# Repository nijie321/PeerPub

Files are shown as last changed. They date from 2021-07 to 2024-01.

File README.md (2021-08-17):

# PeerPub 
 Tracking two rats independently during oral operant self-administration of solutions (e.g. sucrose, alcohol, opioids).

## Program Structure

   Main Program: main.py (main_test.py) is the entry program. This program handles session command and rat ID
   scanning, adjusting the pump position, and finally calling the operant.py as a subprocess.
   Note that this program does not exit after calling the subprocess. It it kept alive, as the
   main thread, to record rat's ID when they poke their head near the antenna. Rat's ID are
   stored in _active and _inactive files located in the /home/pi/ directory.
   
   Operant Program: operant.py (operant_test.py) is the program which main invoke at the end of it's executation.
   This program handles saving each data point to corresponding data files.

   Pump Driver Program: pump_move.py is the program that is used, as a higher level abstraction, to drive the stepper motor using underlying gpiozero/RPi.GPIO library. This program mainly consist of the PumpMove class which contains a move() class for "rotating" the motor (forward and backward). The __del__ method need to be call at the end of each use to 'shutoff' the motor. This prevent the motor driver from overheating (there are more efficient ways to do this).
   
   Activity Counter Program: Rat's activity (inactive lick, active lick, and etc) are being represent as an instance of RatActivityCounter.

   PumpCalibration Program: Currently, the motor step size is not accurate enough. The pump's step need to be modified from time to time. This program prompt the user to measure the amount of solution the pump push out and enter that amount. Then the program will automatically re-adjust the step size.

## Configuration
   - Files

     - /home/pi/peerpub_config.json
        This file stores 3 information: device ID, session number/ID, and stepper motor step size. (The session number is increament by 1 each time the program start)

     - /home/pi/openbehavior/PeerPub/python/session_configuration.csv
        This file is used by the program to read in the session information. 

     - /home/pi/openbehavior/PeerPub/python/config.py
        This file stores different directory paths. Note that these path are all absolute paths. There's a "get_sessioninfo" function which takes in a argument "sessionid" to retrive session information from "session_configuration.csv" mentioned above. A good practice is to put related configuration functions in this file and import then when needed.

## Utility Scripts

   **check_empty_program.sh**: a script that check the size of every python file in the python/ directory. If one or more files are empty the script then reclone the entire repository.

   **check_network.sh**: a script that check the network connection right after the device boots up and ask user for action when the device was not able to connect to network.

## Program Overview
The main (main_test.py) program is used to read/scan the pre-configured command RFID stored in 'session_configuration.csv' file under python directory. After the command ID is scaned, the program proceed to ask for scanning rat's ID. The time between scanning rat's ID and command ID is the time for adjusting the pump position (e.g. after the rat's ID are scanned, the pump adjustment are disabled to avoid driver board overheating). After the rat's ID are scanned, the main program spawns a new operant (operant_test.py) program by passing in the necessary arguments and run it in the background. Note that because the operant program is a thread, the main program is kept alive (e.g. running in parallel with the operant program). The main program is tasked with reading the rat's ID when they poke their head into the active or inactve spout (disctinguished by the length of characters: 10 for inactive poke and 8 for active poke).

## Parts and GPIO Pin Connections Table

   [DRV8834 Low-Voltage Stepper Motor Driver](https://www.pololu.com/product/2134), [Stepper Motor](https://www.pololu.com/product/2267), [Belker Universal AC Adapter 3-12V](https://www.amazon.com/Belker-Adjustable-Universal-Household-Electronics/dp/B07NKZCWT1/ref=asc_df_B07NKZCWT1/?tag=hyprod-20&linkCode=df0&hvadid=366402536789&hvpos=&hvnetw=g&hvrand=9548953669677245441&hvpone=&hvptwo=&hvqmt=&hvdev=c&hvdvcmdl=&hvlocint=&hvlocphy=9013532&hvtargid=pla-800552094134&psc=1&tag=&ref=&adgrpid=75347436439&hvpone=&hvptwo=&hvadid=366402536789&hvpos=&hvnetw=g&hvrand=9548953669677245441&hvqmt=&hvdev=c&hvdvcmdl=&hvlocint=&hvlocphy=9013532&hvtargid=pla-800552094134)
   | Pins on the driver | GPIO pin slot on the Pi, external power supply, and the stepper motor|
   |--------------------|------------------------|
   |      VMOT         |      **AC Adapter** - positive end of LED Terminal Adapter    |
   |     GND |   **AC Adapter** - negative end of LED Terminal Adapter |
   | B2, B1, A1, A2 |    **Stepper Motor** - Black, Green, Red, and Blue wire respectively      |
   |      GND |    **Pi** - Any GND pin                |
   |      M0, M1 | **Pi** - GPIO 17 and 22       |
   |     SLP | **Pi** - Any 3v3 pin          |
   |      STEP | **Pi** - GPIO 6            |
   |      DIR | **Pi** - GPIO 26 |
   
   [Adafruit 12-Key Capacitive Touch Sensor - MPR121](https://www.adafruit.com/product/1982)
   | Pins on the driver | GPIO pin slot on the Pi and external wires|
   |--------------------|------------------------|
   |  SCL, SDA | **Pi** - GPIO 3 and 2 respectively |
   |  3Vo | **Pi** - Any 3v3 pin|
   |  GND | **Pi** - Any GND pin|
   |  0 | **external wire** - inactive wire|
   |  1 | **external wire** - active wire|

   [Limit Switch](https://www.amazon.com/MXRS-Hinge-Momentary-Button-Switch/dp/B07MW2RPJY/ref=lp_5739467011_1_7)
   | Pins on the driver | GPIO pin slot on the Pi and external wires|
   |--------------------|------------------------|
   |  Normally Open (NO) | **Pi** - any 5V pin|
   |  Forward Limit - Contact Point (C) | **Pi** - GPIO 24|
   |  Backward Limit - Contact Point (C) | **Pi** - GPIO 23|

   [Push Button](https://www.amazon.com/DAOKI-Miniature-Momentary-Tactile-Quality/dp/B01CGMP9GY/ref=asc_df_B01CGMP9GY/?tag=hyprod-20&linkCode=df0&hvadid=309774137275&hvpos=&hvnetw=g&hvrand=7843520885449353644&hvpone=&hvptwo=&hvqmt=&hvdev=c&hvdvcmdl=&hvlocint=&hvlocphy=9013532&hvtargid=pla-640514760452&psc=1)
   | Pins on the driver | GPIO pin slot on the Pi|
   |--------------------|------------------------|
   | Forward Button | **Pi** - GPIO 5|
   | Backward Button | **Pi** - GPIO 27|
   **Connect resistor and GND correspondingly**
   
   [Pixel Ring](https://www.adafruit.com/product/1643)
   | Pins on the driver | GPIO pin slot on the Pi|
   |--------------------|------------------------|
   | IN | **Pi** - GPIO 18|
   | GND | **Pi** - any GND pin |
   | 5V DC | **Pi** - any 5V pin |

## Resources
   [Raspberry Pi Stepper Motor Tutorial](https://www.rototron.info/raspberry-pi-stepper-motor-tutorial/)  
   [Raspberry Pi Stepper Motor Control with nema17](https://makersportal.com/blog/raspberry-pi-stepper-motor-control-with-nema-17)  
   [OpenSourceSyringePump](http://cavarnon.com/syringepump)  
   [How to Control a stepper motor with DRV8825 driver and Arduino](https://www.makerguides.com/drv8825-stepper-motor-driver-arduino-tutorial/)

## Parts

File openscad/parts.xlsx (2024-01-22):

Item | Part | Quantity | Supplier | Link
Pump Parts | Pump power | 1 | Amazon | https://www.amazon.com/Belker-Adjustable-Universal-Household-Electronics/dp/B07NKZCWT1
 | NEMA 17 Stepper Motor | 1 | Pololu | https://www.pololu.com/product/2267
 | 12" Actobotics Channel | 1 | ServoCity | https://www.servocity.com/12-0-channel
 | Actobotics Side Tapped Pattern Mount B | 1 | ServoCity | https://www.servocity.com/90-quad-hub-mount-b
 | Actobotics NEMA 17 Stepper Mount | 1 | ServoCity | https://www.servocity.com/nema-17-stepper-motor-mount
 | Pump rod | 1 | Amazon | https://www.amazon.com/uxcell-Stainless-Copper-Thread-Printer/dp/B07R1H5ZMV?s=industrial
 | Rod bearing | 1 | Amazon | https://www.amazon.com/Bearings-Double-Shielded-Miniature-Skateboard/dp/B07H83VV6B
 | Rod coupling | 1 | Amazon | https://www.amazon.com/AFUNTA-Flexible-Couplings-Compatible-Machines/dp/B07JL1QYLS
 | 4 pin connector | 1 | Amazon | https://www.amazon.com/mxuteuk-Female-Connector-Adapter-Electrical/dp/B083GR7FQF
 | 3 pin connector | 1 | Amazon | https://www.amazon.com/BTF-LIGHTING-Connectors-WS2812B-WS2811-WS2812/dp/B01DC0KIT2
 | Limit Switch with Lever 2 Pack | 1 | ServoCity | https://www.servocity.com/spdt-miniature-lever-snap-action-micro-switch-2-pack
Box Parts | Raspberry Pi 3B | 1 | Rasperrypi | https://www.raspberrypi.com/
 | Pi screen | 1 | Dfrobot | https://www.dfrobot.com/product-1784.html
 | Pololu DRV8825 Stepper Motor Driver | 1 | Pololu | https://www.pololu.com/product/2133
 | Touch sensor board | 1 | Adafruit | https://www.adafruit.com/product/1982
 | Button | 1 | Amazon | https://www.amazon.com/Gikfun-12x12x7-3-Tactile-Momentary-Arduino/dp/B01E38OS7K
 | Button board | 1 | Amazon | https://www.amazon.com/LAMPVPATH-Prototype-Breadboard-Universal-Printed/dp/B07JDZDPVQ
 | Led ring | 1 | Adafruit | https://www.adafruit.com/product/2852
 | Rfid scanner | 1 | Amazon | https://www.amazon.com/YARONGTECH-125khz-reader-EM4100-desktop/dp/B078TK8KYL/?th=1
 | connector cables | 1 | Amazon | https://www.amazon.com/Antrader-Breadboard-Dupont-Arduino-Raspberry/dp/B07RXK9SLW?th=1
 | Resistor(200ohm, 1/2w) | 1 | Amazon | https://www.amazon.com/EDGELEC-Resistor-Tolerance-Multiple-Resistance/dp/B07QDXV1KF
Other Parts | 30 cc Syringe 10 pack | 1 | Amazon | https://www.amazon.com/Easy-Glide-30CC-Syringe-Sterile/dp/B08HV25ZN2
 | screw and nuts (#6-32)

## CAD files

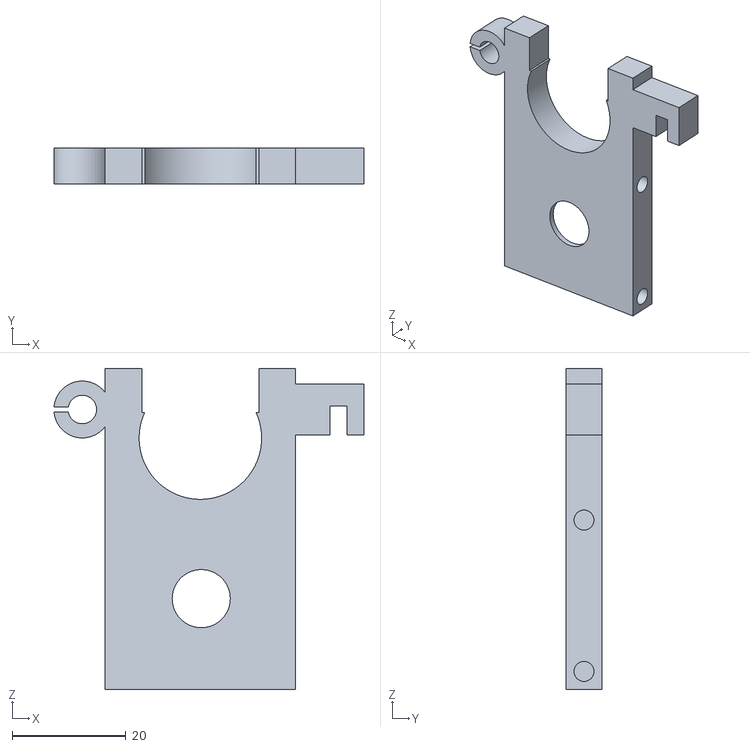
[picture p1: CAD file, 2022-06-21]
openscad/pump_top.stl
54.4 x 6.30 x 56.4

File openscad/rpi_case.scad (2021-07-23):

//include <driverPlate.scad>;
$fn=50;


// define global variables (measurments, unit = mm)
lcdWidth = 121.4 + 25 - 25 ;
lcdWidthForScrewHolder = 121.4 ;
lcdThickness = 7.91;
lcdHeight = 76.80 ;
baseBoardThickness = 2;//.5;


squareHeight=7.5;
squareWidth=7.5;
squareThickness= 1;//2.5;

screwInnerRadius = 1.5;//2.56;
smallChipWidth = 19.18;
smallChipHeight = 33.32;

heightToScrew = 13.15; //12.88

smallChipThickness = 1.69;
smallChipHoleRadius = 2.42;
screenWidth = 109.8;
screenHeight = 66.4 ;

leftSideInputPortsWidth = 50.67;
leftSideInputPortsHeightFromBase = 21.36;
leftSideInputPortsHeight = 8.05;

endInputPortsHeightFromBase = 30.96;
endInputPortsWidth = 52.37;




overallWidth=77.33 ;
    width=72.91 ;
    protrodingWidth=overallWidth - width;
    protrodingThickness=2.2;
    
    
module base(){
rotate([0,90,0]) color("red") cube([baseBoardThickness+1, lcdWidth, lcdHeight], center=true);
}

module makeRearendWall(head=1){

    overallWidth=78.4;
    width=72.91 -2.5;
    protrodingWidth=overallWidth - width;
    protrodingThickness=2.2;
    
    
//    height=77.33;
//    
//    overallWidth=77.33;
//    width=77.48;//72.91;
//    protrodingWidth=overallWidth - width;
//    protrodingThickness=2.2;
    // front wall
    if(head ==  1){
        translate([0,(lcdWidthForScrewHolder/2 - (squareHeight/2)) + (squareHeight/2+(baseBoardThickness+1) /2) ,(width/2) - ((baseBoardThickness+1) /2)]) cube([lcdHeight+((baseBoardThickness+1)*2),baseBoardThickness+1,width],center=true);    
    }
    echo((lcdWidthForScrewHolder/2 - (squareHeight/2)) , lcdWidth, lcdWidth - ((lcdWidthForScrewHolder/2 - (squareHeight/2))))
    
    // end wall
    if(head == 0){
//    ((width/2)-((protrodingThickness)/2))    
                translate([0,-(((protrodingThickness) /2)+(lcdWidth/2)),width/2-(baseBoardThickness-1)]) cube([lcdHeight+((baseBoardThickness+1)*2),protrodingThickness,width ],center=true);
    }
    
}



module slider(){
    width = 77.37;
    height = 41.26;
    thickness = 2.11;        
    
    color("red") translate([0,0,lcdHeight/2 + (thickness/2) + (baseBoardThickness/2)]) cube([height, width,thickness],center=true);    
}


module makeTopBottomCover(top=true){
    overallWidth=78.4 ;
    width=72.91 ;
    protrodingWidth=overallWidth - width;
    protrodingThickness=2.2;
   if(top){
       // lcdHeight/2
       
//        (lcdWidth) +(baseBoardThickness+1)*2
   translate([0,0,width - (baseBoardThickness) -1]) cube([lcdHeight+((baseBoardThickness+1) *2), lcdWidth , baseBoardThickness+1],center=true);    
   }
   
   if(!top){
       //+ ((baseBoardThickness+1) *2)
       cube([lcdHeight+((baseBoardThickness+1) *2), (lcdWidth) ,baseBoardThickness+1],center=true);
   }
   
}

cutoff1 = (lcdHeight/2) + (baseBoardThickness/2);
xTempVar = ( (lcdHeight/2) + (baseBoardThickness/2) ) + ( ( (lcdHeight+((baseBoardThickness+1)*2)) )/2 - (cutoff1+ (baseBoardThickness/2) ) ) /2;
yTempVar = -( (lcdWidth/2) + ((baseBoardThickness/2)) + ( ((baseBoardThickness+1)/2) - (baseBoardThickness/2) ) );
zTempVar = 40;

module fourVerticalPoles(topPoles=true, head=true){
    radius = 1.50;//baseBoardThickness/2;
if(topPoles){

if(head){
color("red") translate([xTempVar, yTempVar, zTempVar]) cylinder(r=radius,h=20,center=true);
color("red") translate([-xTempVar, yTempVar, zTempVar]) cylinder(r=radius,h=20,center=true);
}
else{
color("red") translate([xTempVar, -yTempVar, zTempVar]) cylinder(r=radius,h=20,center=true);
color("red") translate([-xTempVar, -yTempVar, zTempVar]) cylinder(r=radius,h=20,center=true);
}

}

if(!topPoles){
color("red") translate([xTempVar,yTempVar,0]) cylinder(r=baseBoardThickness/3,h=20,center=true);
color("red") translate([-xTempVar,yTempVar,0]) cylinder(r=baseBoardThickness/3,h=20,center=true);
}

}

//color("blue") cube([lcdHeight+((baseBoardThickness+1) *2), (lcdWidth + ((baseBoardThickness+1) *2)) ,baseBoardThickness+1],center=true);


depth = squareThickness + 10;
module placeScrewHolder(x=(lcdHeight/2 - (squareWidth/2)) , y=(lcdWidthForScrewHolder/2 - (squareHeight/2)) , z=squareThickness * 1.5 + 15.6, rearEnd=false, flag=1) {
    
    if(rearEnd==false){
    
    translate([x,y,z])
    difference(){
            cube([squareWidth,squareHeight,squareThickness],center=true);
            color("blue") cylinder(r=screwInnerRadius,h=squareThickness,center=true);
    }
    
    }
    
    if(rearEnd==true){
        if(flag == 1){
            translate([x,y,z])
            difference(){
                    cube([squareWidth+1,squareHeight+1,squareThickness],center=true);
                    color("blue") translate([1,-1,0]) cylinder(r=screwInnerRadius+.1,h=squareThickness,center=true);    
            }
        }
            
        if(flag == 2){
            translate([x,y,z])
            difference(){
                    cube([squareWidth+1,squareHeight+1,squareThickness],center=true);
                    color("blue") translate([-1,-1,0]) cylinder(r=screwInnerRadius+.1,h=squareThickness,center=true);            
        }
    }
    }
}

module placeCornerScrewHolder(x=0,y=0,z=0){
    translate([x,y,z])
    difference(){
    color("red") cube([squareWidth,squareHeight,depth],center=true);
    translate([0,0,(depth/2)/2]) color("blue") cylinder(r=screwInnerRadius,h=depth/2,center=true);
    }
}

//placeScrewHolder(x=(lcdHeight/2 - (squareWidth/2)),y=(lcdWidth/2 - (squareHeight/2)),z=((baseBoardThickness+1)/2) + (squareThickness/2) + heightToScrew);


toTranslateX = (lcdHeight/2) - (squareWidth/2);
toTranslateY = (lcdWidth/2) - (squareHeight/2);
//toTranslateZ = (lcdHeight/2) - ((baseBoardThickness+1)/2) - (depth/2);
//toTranslateZ =  depth/2 + ((baseBoardThickness+1)/2) + depth + width/2 + baseBoardThickness+1;
toTranslateZ = 1.5*depth + 1.5*(baseBoardThickness+1) + width/2 + 5.4;//2.5;

toTranslateYBottom = ( (lcdWidth/2) - (depth/2));
toTranslateZBottom =   (squareHeight/2) + ( (baseBoardThickness+1) / 2) + 15;
module makeScrewHolders(){
    
translate([0,0,-1.3]) union(){
    placeScrewHolder(rearEnd=true,flag=2);

    placeScrewHolder(x=-(lcdHeight/2 - (squareWidth/2)), rearEnd=true);
        

    placeScrewHolder(y= -(lcdWidthForScrewHolder/2 - (squareHeight/2) ) );

    placeScrewHolder(x=-(lcdHeight/2 - (squareWidth/2)),y=-(lcdWidthForScrewHolder/2 - (squareHeight/2)));
}
//placeScrewHolder(y=-(lcdWidth/2 - (squareHeight/2)));



// top four screw holder
//placeCornerScrewHolder(x=toTranslateX,y=-toTranslateY,z=toTranslateZ - 2.5);
placeCornerScrewHolder(x=toTranslateX,y=(lcdWidthForScrewHolder/2 - (squareHeight/2)),z=toTranslateZ - 2.5);
    
placeCornerScrewHolder(x=-toTranslateX,y=-toTranslateY + 11,z=toTranslateZ - 2.5);        
//placeCornerScrewHolder(x=-toTranslateX,y=(lcdWidthForScrewHolder/2 - (squareHeight/2)),z=toTranslateZ - 2.5); 

 

translate([toTranslateX,-toTranslateYBottom, toTranslateZBottom + heightToScrew]) rotate([90,0,0]) placeCornerScrewHolder();
translate([-toTranslateX,-toTranslateYBottom,toTranslateZBottom + heightToScrew]) rotate([90,0,0]) placeCornerScrewHolder();


color("green") translate([toTranslateX,-toTranslateYBottom, toTranslateZBottom + heightToScrew + 28.70]) rotate([90,0,0]) placeCornerScrewHolder();
color("green") translate([-toTranslateX,-toTranslateYBottom,toTranslateZBottom + heightToScrew + 28.70]) rotate([90,0,0]) placeCornerScrewHolder();       
}

extraBoardWidth = (smallChipHeight * 2) + 10;
extraBoardHeight = smallChipWidth + 5;

module extraBaseExtensions(){
// add extra base to hold two additional modules

//color("blue") translate([lcdHeight/2 + (smallChipWidth/2) + 5 ,0,0]) 
    cube([extraBoardHeight, ( (baseBoardThickness+1) *2) + (lcdHeight),(baseBoardThickness+1)], center=true);
}

GPIOSlotsWidth = 50.76/2;
GPIOSlotsHeight = 12.5;


module makeChipSlot(firstSlot=true){
    if(firstSlot){
translate([0,(smallChipHeight/2 + ((baseBoardThickness+1)/2) ),((baseBoardThickness+1) /2)- (smallChipThickness/2)]) cube([smallChipWidth,smallChipHeight,smallChipThickness],center=true);    
        }
        
     if(!firstSlot){
         translate([0,-(smallChipHeight/2 +((baseBoardThickness+1)/2)) ,((baseBoardThickness+1) /2) - (smallChipThickness/2)]) cube([smallChipWidth,smallChipHeight,smallChipThickness],center=true);
     }

}



h1 = (baseBoardThickness+1) - (smallChipThickness);

// extended base with two slots for the two additional sensors.
module sensorSpace(){
    
difference(){
    
difference(){
// extended base (to end)
extraBaseExtensions();
    // making slots for two sensors
    makeChipSlot(firstSlot=true);
    makeChipSlot(firstSlot=false);
}

// make four holes for the purpose of mounting two sensors.
#translate([(smallChipWidth/2) - (smallChipHoleRadius), (smallChipHeight / 2)+ (smallChipHeight/2 + ((baseBoardThickness+1)/2) ) - (smallChipHoleRadius), -(h1/2) - (smallChipThickness - ((baseBoardThickness+1) /2))]) cylinder(r=smallChipHoleRadius - 0.5,h=h1,center=true);
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

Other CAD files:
openscad/pump_mid.stl

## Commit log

2021-07-16 update instruction for calibration
2021-07-23 Add files via upload
    raspberry pi 3d design case
    [rpi_case.scad]
2022-01-13 push syringe to wet spout
2022-02-25 add FR 2mins for quick device test
    [session_configuration.csv]
2022-05-04 add Fr5 8hrs key
    [session_configuration.csv]
2022-06-21 update pump files
    [pump_mid.stl, pump_top.stl]
2024-01-22 add parts list file
    [parts.xlsx]
